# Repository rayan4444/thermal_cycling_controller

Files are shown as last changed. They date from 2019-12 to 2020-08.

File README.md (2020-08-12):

# UPCR TEC Module

RS-422 enabled module for bidirectional control of up to 2 TEC modules.
Refer to individual directories README for more details.

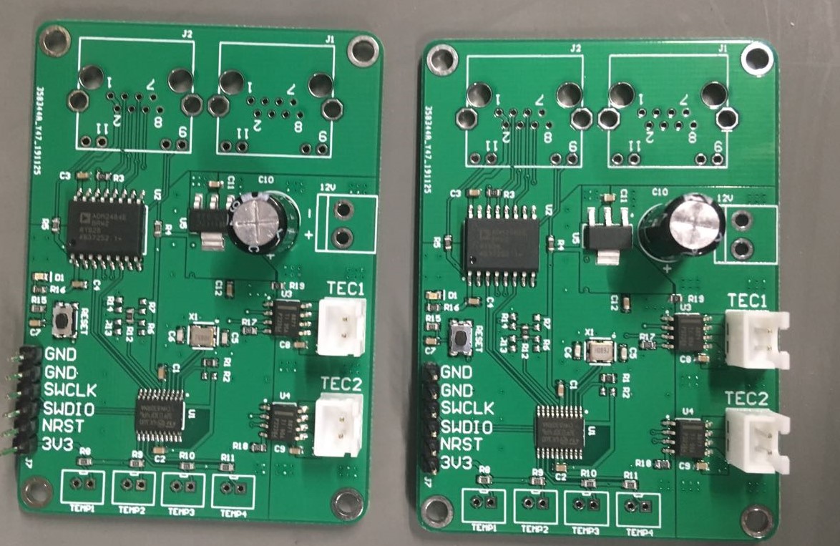
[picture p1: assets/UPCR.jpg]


## Features
* 4 NTC temperature sensors
* 2 biderectional TEC drivers (12V input)
* Isolated RS-422 Bus
* STM32F030F4 on board microcontroller

## Hardware
This repository contains
* Altium Designer files
* BOM
* Schematic PDF
Gerber files are available in releases

## Firmware
The code in this repository handles the general workflow of the module.
* STM32 Cube MX project
* Makefile
* Source code
* Python script to generate temperature lookup table
> To use this code you will need to define the communication protocol between devices (number of bytes, message structure) as well as tune the PID loop for temperature control.

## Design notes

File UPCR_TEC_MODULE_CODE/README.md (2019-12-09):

# UPCR TEC Module Firmware

## Workflow 
UART: 
* wait for communication
* store incoming data into DMA rx_buffer
* once the rx_buffer is full, trigger an interrupt to raise the ```new_rx_data_flag``` 
* copy rx_buffer data into another variable to avoid getting it overwritten
* [do stuff depending on the protocol you define]
    * in my example: T 62 0 0 starts PID temperature control to 62 deg C
    * in my example: S 0  0 0 stops the PID temperature control

ADC:  
* If PID control is enabled, enable timer 16
* Timer 16 sets interrupts to triger ADC sampling
* ADC read all 4 temperature sensor channels and stores data into DMA buffer
* when the DMA buffer is full, trigger an interrupt to raise the ``` dma_adc_status_flag```
* use the corresponding data as ```Input``` for your PID loop

PID: 
> because the chip has a very small flash memory, we cannot use floating point maths to run our PID loop. 
* Convert temperature received from UART to 100th od degrees 
* find the equivalent ADC value in the temperature lookup table
    * the temperature lookup table is generated using NTC equations with a python script in ```temperature lookup table generator```
* use this equivalent as ```Setpoint``` in the PID loop
* [tune PID loop coefficients in ```NTC.h```] 

## Tools, Tutorials and References
* [STM32 CubeMX](https://www.st.com/en/development-tools/stm32cubemx.html)
* [Known bug](https://community.st.com/s/question/0D50X0000BbMcnpSQC/dma-adc-doesnt-work) 
* [Tutorials](https://letanphuc.net/)

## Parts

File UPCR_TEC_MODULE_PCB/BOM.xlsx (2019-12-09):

# | Part | Value | Quantity | Comment | Footprint
1 | R17, R18 | 20k | 2 | R | R0603
2 | R15 | 10K | 1 | R | R0603
3 | R8, R9, R10, R11 | 10k/0.1% | 4 | R | R0603
4 | R4, R5, R16 | 3.3K | 3 | R | R0603
5 | R3 | 120R | 1 | R | R0603
6 | R2, R6, R7, R12, R13, R14 | DNP | 6 | R | R0603
7 | R1, R19 | 0R | 2 | R | R0603
8 | C5, C6 | 18pF | 2 | C | C0603
9 | C1, C2, C3, C4, C7, C8, C9, C11, C12 | 100nF | 9 | C | C0603
10 | C10 | 47uF | 1 |  | CPOL_8x9
11 | J7 |  | 1 | CONN_6P | 2.54 6P Header
12 | J2 |  | 1 | RJ45_CONN | RJ45_CONN_V1
13 | J1 |  | 1 | RJ45_CONN | RJ45_CONN_V1
14 | D1 |  | 1 | LED | 0603 LED
15 | X1 |  | 1 | 8MHz | CRYSTAL_4P_3.2X2.5
16 | U5 |  | 1 | LM1117 3.3v | SOT223
17 | U3,U4 |  | 2 | DRV8871 | DRV8871- SOIC8
19 | U2 |  | 1 | ADM2484E | ADM2484-SOIC16
20 | U1 |  | 1 | STM32F030F4 | STM32F030F4- TSSOP20
24 | TEMP1, TEMP2, TEMP3, TEMP4 |  | 4 | CONN_2P | JST B2B-PH-K-S
26 | TEC1, TEC2 |  | 2 | CONN_2P | JST B2B-XH-A - THIN PADS
27 | RESET |  | 1 | KMR2 | KMR2_tact_switch

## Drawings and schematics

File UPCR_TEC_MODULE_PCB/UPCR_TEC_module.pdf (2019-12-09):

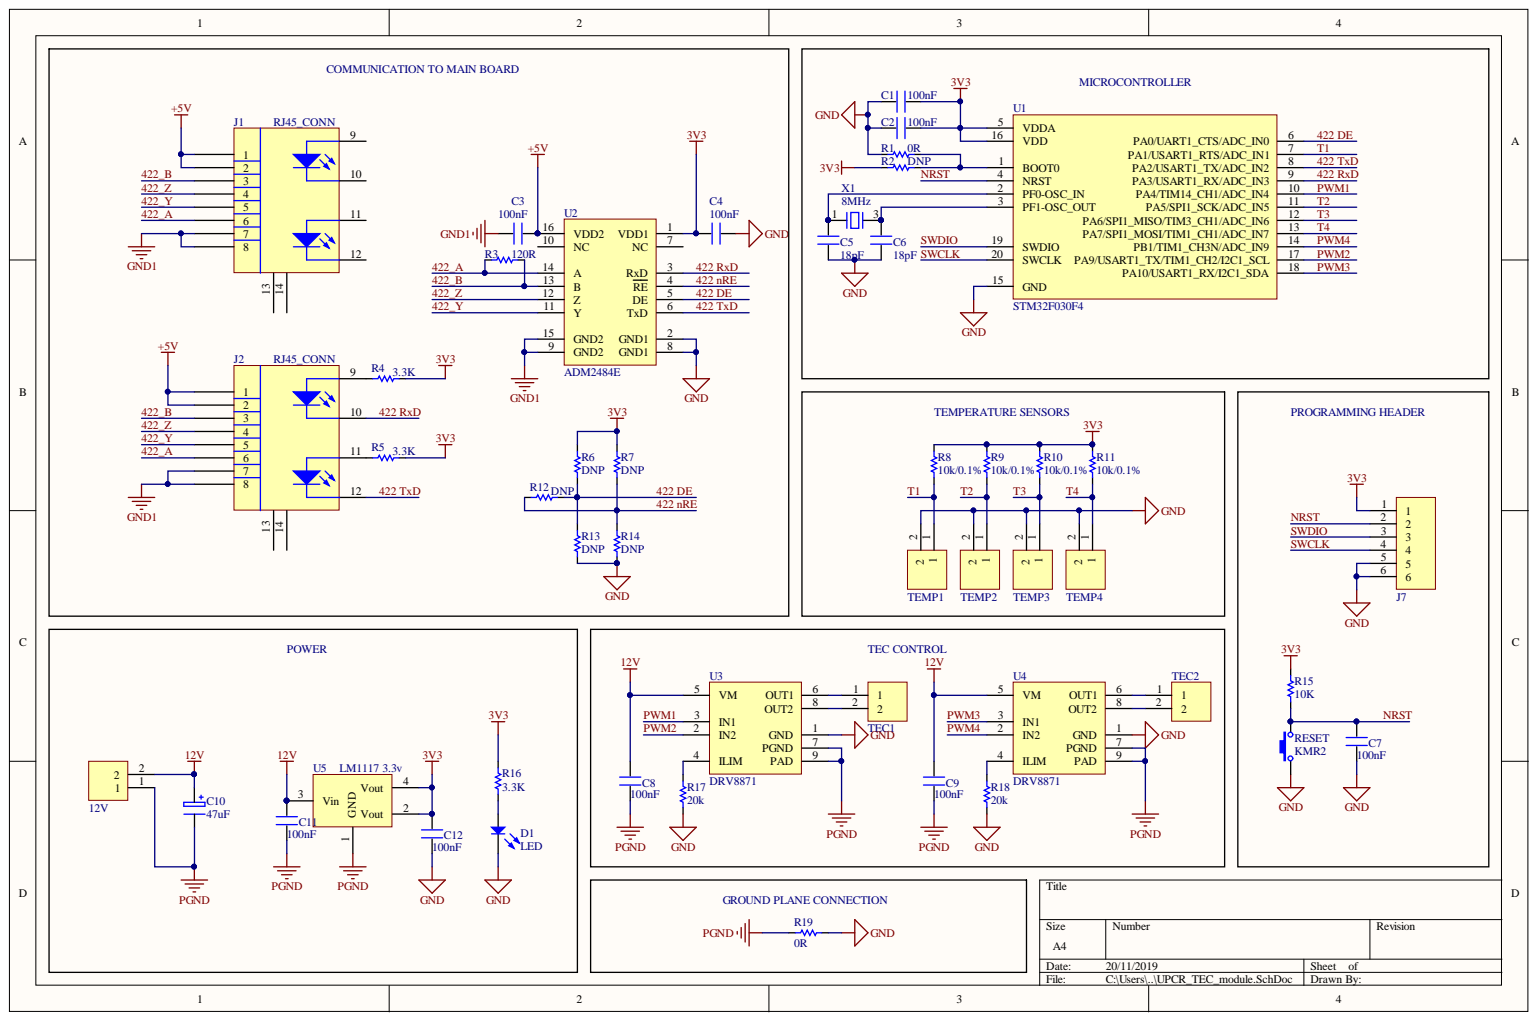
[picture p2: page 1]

COMMUNICATION TO MAIN BOARD

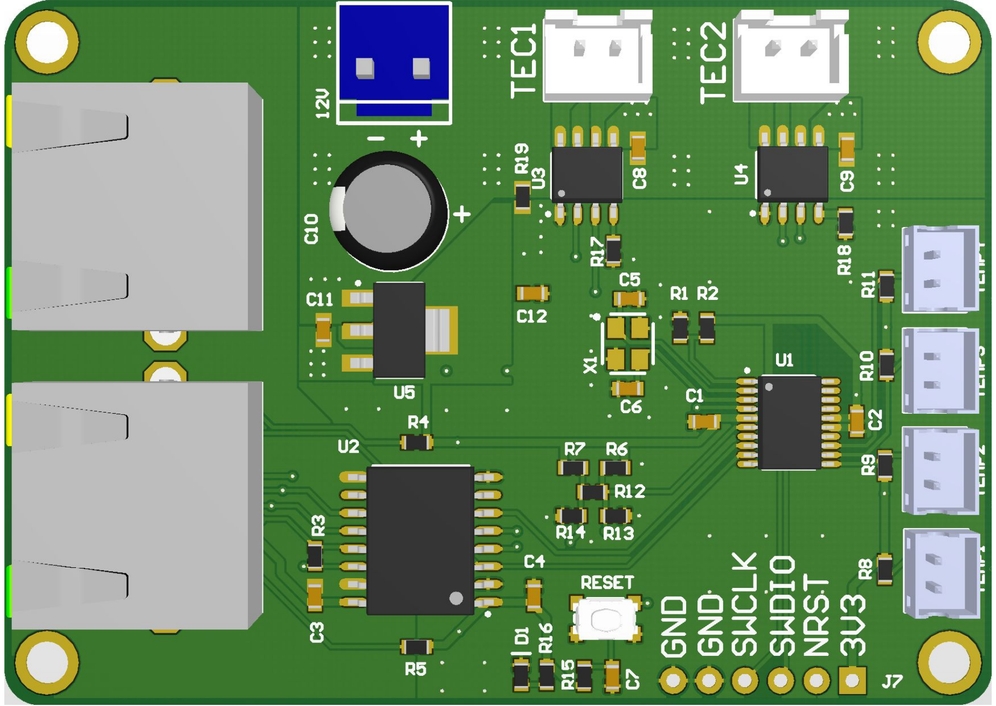
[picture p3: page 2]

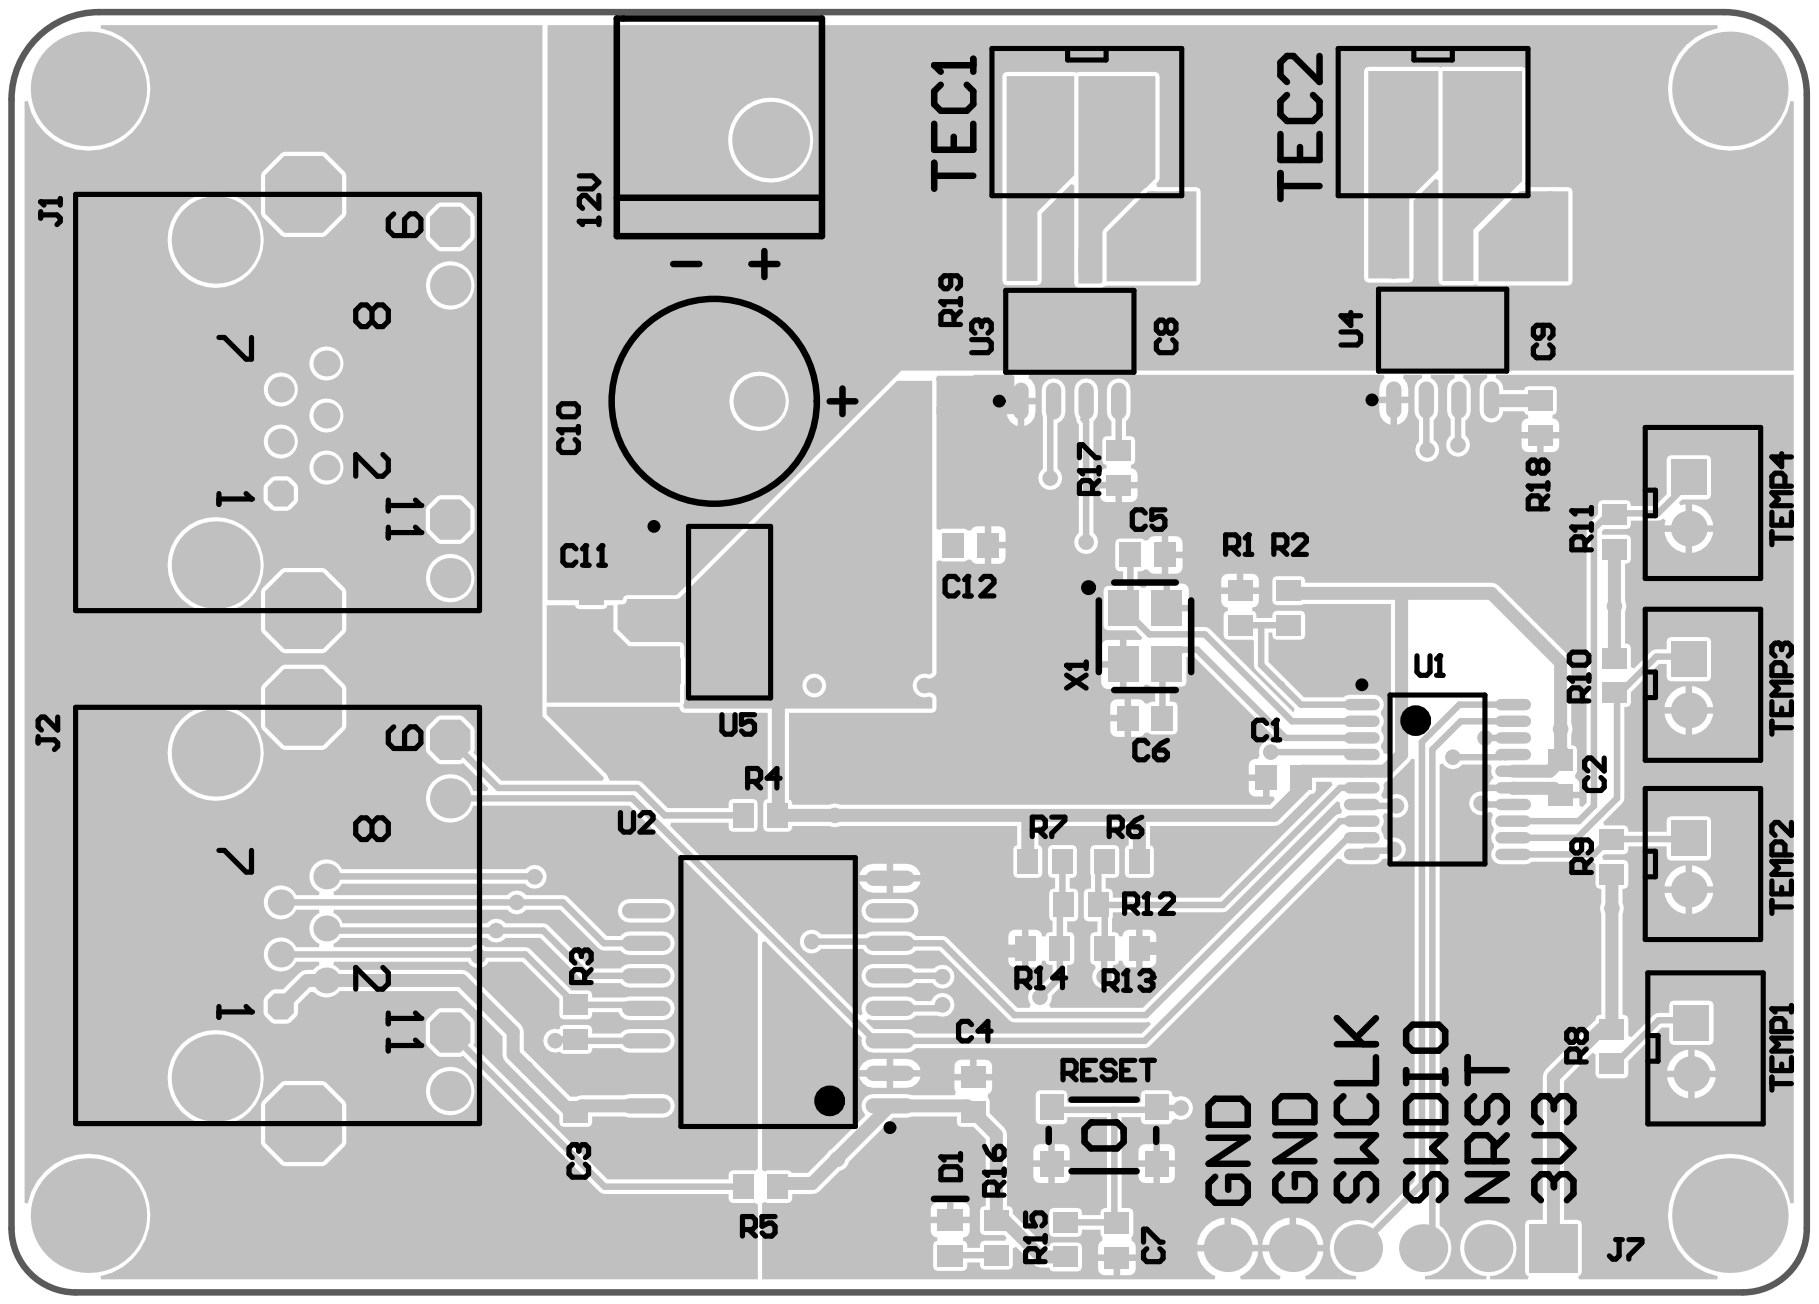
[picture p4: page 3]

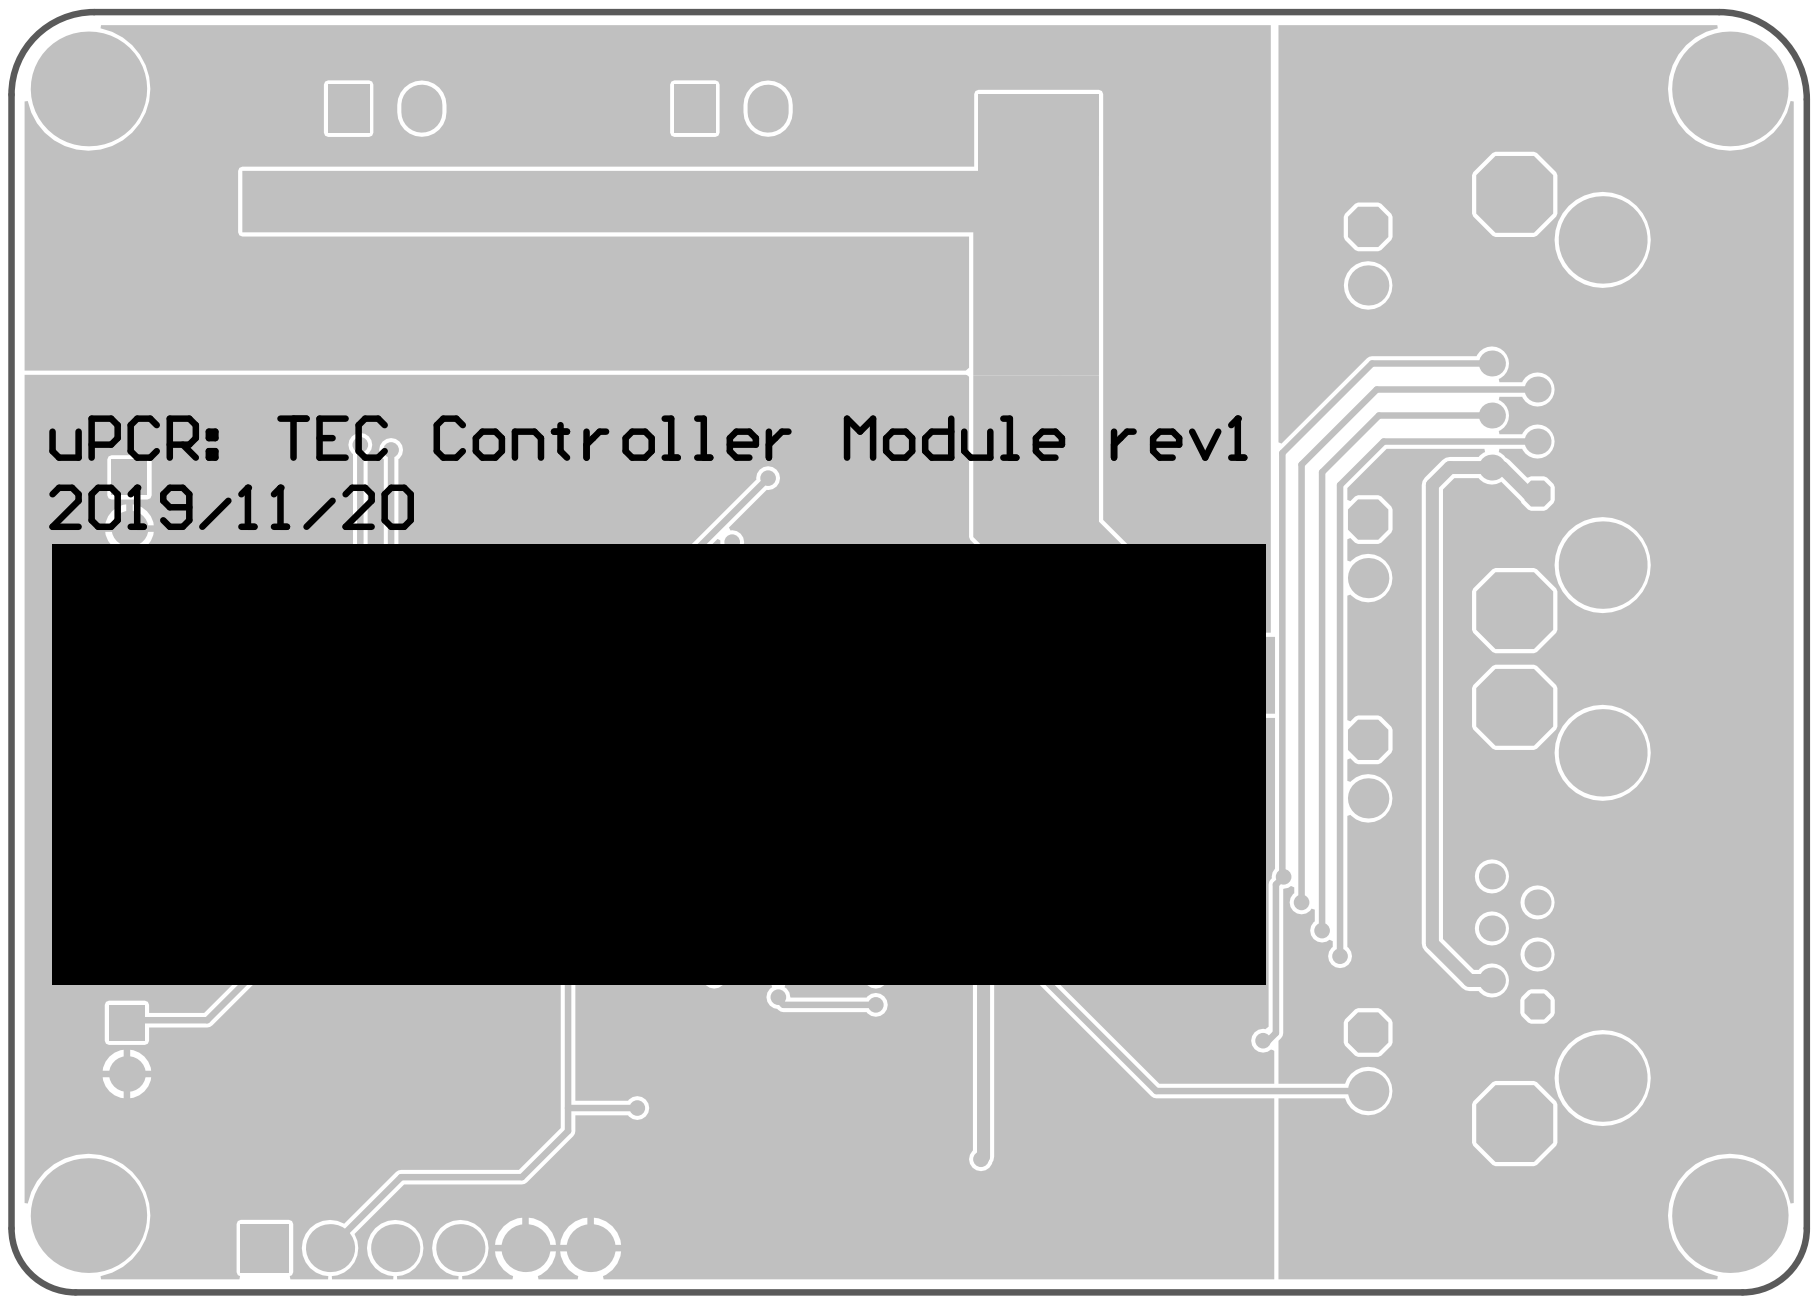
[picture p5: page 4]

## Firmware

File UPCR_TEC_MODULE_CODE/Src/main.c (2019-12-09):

/* USER CODE BEGIN Header */
/**
  ******************************************************************************
  * @file           : main.c
  * @brief          : Main program body
  ******************************************************************************
  * @attention
  *
  * <h2><center>&copy; Copyright (c) 2019 STMicroelectronics.
  * All rights reserved.</center></h2>
  *
  * This software component is licensed by ST under BSD 3-Clause license,
  * the "License"; You may not use this file except in compliance with the
  * License. You may obtain a copy of the License at:
  *                        opensource.org/licenses/BSD-3-Clause
  *
  ******************************************************************************
  */
/* USER CODE END Header */

/* Includes ------------------------------------------------------------------*/
#include "main.h"

/* Private includes ----------------------------------------------------------*/
/* USER CODE BEGIN Includes */
#include "NTC.h"
#include "stm32f0xx_it.h"
#include <stdio.h>
#include <string.h>

/* USER CODE END Includes */

/* Private typedef -----------------------------------------------------------*/
/* USER CODE BEGIN PTD */

/* USER CODE END PTD */

/* Private define ------------------------------------------------------------*/
/* USER CODE BEGIN PD */

/* USER CODE END PD */

/* Private macro -------------------------------------------------------------*/
/* USER CODE BEGIN PM */

/* USER CODE END PM */

/* Private variables ---------------------------------------------------------*/
ADC_HandleTypeDef hadc;
DMA_HandleTypeDef hdma_adc;

TIM_HandleTypeDef htim1;
TIM_HandleTypeDef htim3;
TIM_HandleTypeDef htim14;
TIM_HandleTypeDef htim16;

UART_HandleTypeDef huart1;
DMA_HandleTypeDef hdma_usart1_rx;

/* USER CODE BEGIN PV */
volatile int enable_pid_flag, dma_adc_status_flag, new_rx_data_flag;
uint32_t new_adc_reading[4], read_adc[4]; // containers for DMA buffer and extracting data from it

uint16_t Setpoint;
uint8_t rx_buffer[4], data[4];

/* USER CODE END PV */

/* Private function prototypes -----------------------------------------------*/
void SystemClock_Config(void);
static void MX_GPIO_Init(void);
static void MX_ADC_Init(void);
static void MX_TIM1_Init(void);
static void MX_TIM3_Init(void);
static void MX_TIM14_Init(void);
static void MX_USART1_UART_Init(void);
static void MX_TIM16_Init(void);
static void MX_DMA_Init(void);
/* USER CODE BEGIN PFP */
void pwm_set_value(uint8_t channel, uint16_t value);
void calibrateADC(); // remove ADC offset

/* USER CODE END PFP */

/* Private user code ---------------------------------------------------------*/
/* USER CODE BEGIN 0 */
void HAL_TIM_PeriodElapsedCallback(TIM_HandleTypeDef* htim)
{
    if (htim->Instance == TIM16) {
        HAL_ADC_Start_DMA(&hadc, new_adc_reading, 4);
    }
}

void HAL_ADC_ConvCpltCallback(ADC_HandleTypeDef* hadc)
{
    //despite its name this funciton gets called when the  DMA transfer complete interrupt is triggered
    dma_adc_status_flag = 1;
}
void HAL_UART_RxCpltCallback(UART_HandleTypeDef* huart)
{
    //this happens when the receive buffer is full
    new_rx_data_flag = 1;
}

/* USER CODE END 0 */

/**
  * @brief  The application entry point.
  * @retval int
  */
int main(void)
{
    /* USER CODE BEGIN 1 */

    /* USER CODE END 1 */

    /* MCU Configuration--------------------------------------------------------*/

    /* Reset of all peripherals, Initializes the Flash interface and the Systick. */
    HAL_Init();

    /* USER CODE BEGIN Init */

    /* USER CODE END Init */

    /* Configure the system clock */
    SystemClock_Config();

    /* USER CODE BEGIN SysInit */

    /* USER CODE END SysInit */

    /* Initialize all configured peripherals */
    MX_GPIO_Init();
    MX_ADC_Init();
    MX_TIM1_Init();
    MX_TIM3_Init();
    MX_TIM14_Init();
    MX_USART1_UART_Init();
    MX_TIM16_Init();
    MX_DMA_Init();
    /* USER CODE BEGIN 2 */
    HAL_ADC_MspInit(&hadc); // I need to call this function again because of a STM32CubeMX bug: when MX_DMA_Init runs it breaks the DMA settings done in the ADC so we have to reconfiure it later
    HAL_UART_MspInit(&huart1); // same, STM32DubeMX bug.
    HAL_TIM_Base_Start_IT(&htim16); //enable timer 16 with interrupt
    HAL_GPIO_WritePin(GPIOA, GPIO_PIN_0, 1); // enable RX and TX
    HAL_UART_Receive_DMA(&huart1, rx_buffer, sizeof(rx_buffer));

    /* USER CODE END 2 */

    /* Infinite loop */
    /* USER CODE BEGIN WHILE */
    while (1) {
      

        if (new_rx_data_flag == 1) {
            //new data is available in the DMA buffer, pull it out before it gets overwritten
            memcpy(data, rx_buffer, sizeof(rx_buffer));
            new_rx_data_flag = 0; //reset flag
            if (data[0] == 0x54) // if Byte 1= "T" for Temperature  T->0x54
            {
                Setpoint = (uint16_t)data[1];
                enable_pid_flag = 1;
            }

            if (data[0] == 0x53) // if Byte 1= "S" for Stop  S->0x53
            {
                enable_pid_flag = 0;
            }
        }

        if ((dma_adc_status_flag == 1) && (enable_pid_flag == 1)) {
            // reset the flag
            dma_adc_status_flag = 0;
            //new data is available in the DMA buffer, pull it out before it gets overwritten
            memcpy(read_adc, new_adc_reading, sizeof(read_adc));

            // run PID function
            int32_t result = compute_temp_PID(Setpoint, read_adc[0]);

            //set Output PWM
            // if result is positive: run the heater, turn off the cooler
            // if result is negative: run the cooler, turn off the heater
            // we assume the heater is connected to TEC1 and the Cooler to TEC2
            if (result >= 0) {
                pwm_set_value(1, result);
                pwm_set_value(3, 0);
            } else {
                pwm_set_value(1, 0);
                pwm_set_value(3, -result);
            }
        }

        /* USER CODE END WHILE */

        /* USER CODE BEGIN 3 */
    }
    /* USER CODE END 3 */
}

/**
  * @brief System Clock Configuration
  * @retval None
  */
void SystemClock_Config(void)
{
    RCC_OscInitTypeDef RCC_OscInitStruct = { 0 };
    RCC_ClkInitTypeDef RCC_ClkInitStruct = { 0 };
    RCC_PeriphCLKInitTypeDef PeriphClkInit = { 0 };

    /** Initializes the CPU, AHB and APB busses clocks 
  */
    RCC_OscInitStruct.OscillatorType = RCC_OSCILLATORTYPE_HSI | RCC_OSCILLATORTYPE_HSI14;
    RCC_OscInitStruct.HSIState = RCC_HSI_ON;
    RCC_OscInitStruct.HSI14State = RCC_HSI14_ON;
    RCC_OscInitStruct.HSICalibrationValue = RCC_HSICALIBRATION_DEFAULT;
    RCC_OscInitStruct.HSI14CalibrationValue = 16;
    RCC_OscInitStruct.PLL.PLLState = RCC_PLL_ON;
    RCC_OscInitStruct.PLL.PLLSource = RCC_PLLSOURCE_HSI;
    RCC_OscInitStruct.PLL.PLLMUL = RCC_PLL_MUL12;
    RCC_OscInitStruct.PLL.PREDIV = RCC_PREDIV_DIV1;
    if (HAL_RCC_OscConfig(&RCC_OscInitStruct) != HAL_OK) {
        Error_Handler();
    }
    /** Initializes the CPU, AHB and APB busses clocks 
  */
    RCC_ClkInitStruct.ClockType = RCC_CLOCKTYPE_HCLK | RCC_CLOCKTYPE_SYSCLK
        | RCC_CLOCKTYPE_PCLK1;
    RCC_ClkInitStruct.SYSCLKSource = RCC_SYSCLKSOURCE_PLLCLK;
    RCC_ClkInitStruct.AHBCLKDivider = RCC_SYSCLK_DIV1;
    RCC_ClkInitStruct.APB1CLKDivider = RCC_HCLK_DIV1;

    if (HAL_RCC_ClockConfig(&RCC_ClkInitStruct, FLASH_LATENCY_1) != HAL_OK) {
        Error_Handler();
    }
    PeriphClkInit.PeriphClockSelection = RCC_PERIPHCLK_USART1;
    PeriphClkInit.Usart1ClockSelection = RCC_USART1CLKSOURCE_PCLK1;
    if (HAL_RCCEx_PeriphCLKConfig(&PeriphClkInit) != HAL_OK) {
        Error_Handler();
    }
}

/**
  * @brief ADC Initialization Function
  * @param None
  * @retval None
  */
static void MX_ADC_Init(void)
{

    /* USER CODE BEGIN ADC_Init 0 */

    /* USER CODE END ADC_Init 0 */

    ADC_ChannelConfTypeDef sConfig = { 0 };

    /* USER CODE BEGIN ADC_Init 1 */

    /* USER CODE END ADC_Init 1 */
    /** Configure the global features of the ADC (Clock, Resolution, Data Alignment and number of conversion) 
  */
    hadc.Instance = ADC1;
    hadc.Init.ClockPrescaler = ADC_CLOCK_ASYNC_DIV1;
    hadc.Init.Resolution = ADC_RESOLUTION_12B;
    hadc.Init.DataAlign = ADC_DATAALIGN_RIGHT;
    hadc.Init.ScanConvMode = ADC_SCAN_DIRECTION_FORWARD;
    hadc.Init.EOCSelection = ADC_EOC_SEQ_CONV;
    hadc.Init.LowPowerAutoWait = DISABLE;
    hadc.Init.LowPowerAutoPowerOff = DISABLE;
    hadc.Init.ContinuousConvMode = DISABLE;
    hadc.Init.DiscontinuousConvMode = DISABLE;
    hadc.Init.ExternalTrigConv = ADC_SOFTWARE_START;
    hadc.Init.ExternalTrigConvEdge = ADC_EXTERNALTRIGCONVEDGE_NONE;
    hadc.Init.DMAContinuousRequests = ENABLE;
    hadc.Init.Overrun = ADC_OVR_DATA_OVERWRITTEN;
    if (HAL_ADC_Init(&hadc) != HAL_OK) {
        Error_Handler();
    }
    /** Configure for the selected ADC regular channel to be converted. 
  */
    sConfig.Channel = ADC_CHANNEL_1;
    sConfig.Rank = ADC_RANK_CHANNEL_NUMBER;
    sConfig.SamplingTime = ADC_SAMPLETIME_239CYCLES_5;
    if (HAL_ADC_ConfigChannel(&hadc, &sConfig) != HAL_OK) {
        Error_Handler();
    }
    /** Configure for the selected ADC regular channel to be converted. 
  */
    sConfig.Channel = ADC_CHANNEL_5;
    if (HAL_ADC_ConfigChannel(&hadc, &sConfig) != HAL_OK) {
        Error_Handler();
    }
    /** Configure for the selected ADC regular channel to be converted. 
  */
    sConfig.Channel = ADC_CHANNEL_6;
    if (HAL_ADC_ConfigChannel(&hadc, &sConfig) != HAL_OK) {
        Error_Handler();
    }
    /** Configure for the selected ADC regular channel to be converted. 
  */
    sConfig.Channel = ADC_CHANNEL_7;
    if (HAL_ADC_ConfigChannel(&hadc, &sConfig) != HAL_OK) {
        Error_Handler();
    }
    /* USER CODE BEGIN ADC_Init 2 */

    calibrateADC();
    /* USER CODE END ADC_Init 2 */
}
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

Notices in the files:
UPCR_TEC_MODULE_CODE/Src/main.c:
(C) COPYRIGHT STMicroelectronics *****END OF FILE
